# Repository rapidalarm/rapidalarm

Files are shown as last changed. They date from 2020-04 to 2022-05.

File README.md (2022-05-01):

# Illinois RapidAlarm: Emergency ventilator sensor and alarm system

*Developed at the Grainger College of Engineering at the University of Illinois at Urbana-Champaign with support from Carle Health and Creative Thermal Solutions, Inc.*

Illinois RapidAlarm

The Illinois RapidAlarm is a sensor and alarm module for use with emergency pressure-cycled ventilators such as the [Illinois RapidVent](https://rapidvent.grainger.illinois.edu/). More information and documentation is available at the [Illinois RapidAlarm project website](http://rapidalarm.github.io).

2020 Copyright University of Illinois Board of Trustees. Software is licensed under the MIT License; all other designs and documentation are licensed under the CC BY 4.0 license: https://creativecommons.org/licenses/by/4.0/

Please see the [legal disclaimer](https://rapidalarm.github.io/#!legal.md) on the project website.

### Repository Structure

- `code/` - firmware for monitor ATMega, simulations
  - `data/` - labeled alarm test data from artificial lung
  - `firmware/` - ATmega328 alarm firmware
  - `rapidalarm/` - Python plotting tools and test suite
- `cad/` - mechanical CAD files, enclosures, etc.
    - `enclosure_lasercut/` - enclosure design files for lasercutter
    - `enclosure_3dprint/` - enclosure design files for 3d printer
- `pcb/` - KiCAD design files
  - `pcb_proto/` - through hole board variant, based on ATmega328
  - `pcb_smd/` - surface mount board variant, based on ATmega32u4

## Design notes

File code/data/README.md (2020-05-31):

# rapidalarm test data

### File structure

- `raw/` - raw data recordings
- `ventmap_0282.csv` - Human trial data converted from ventMAP

### CSV Format

The first two lines of the CSV file contain information about sample rate and column names

e.g.

    #samplerate,50
    pressure,flow,true_pip,true_peep,true_rr
    10.57,3.44,20.57,10.879999999999999,14.084507042253522
    10.55,5.36,20.57,10.879999999999999,14.084507042253522
    10.51,9.18,20.57,10.879999999999999,14.084507042253522
    ...
    
`true_pip`, `true_peep`, `true_rr` refer to reported values from the professional ventilator.  Only available in the ventmap datasets.

### ventMAP Data

A lot of human-trial ventilator waveform data can be found in the [ventMAP project repo](https://github.com/hahnicity/ventMAP/tree/master/ventmap/tests/samples), albeit a bit disorganized.  This includes waveforms from a few modes of ventilation.

These recordings were made using the PB-840 ventilator at 50Hz.  You can use the `ventmap2csv.py` tool to convert these `.csv_test` files into the csv format used by the rapidalarm Python library.

    python ventmap2csv.py raw/ventmap/0282dbl_diff.csv_test ventmap_0282.csv

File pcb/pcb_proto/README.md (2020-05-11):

# pcb_proto

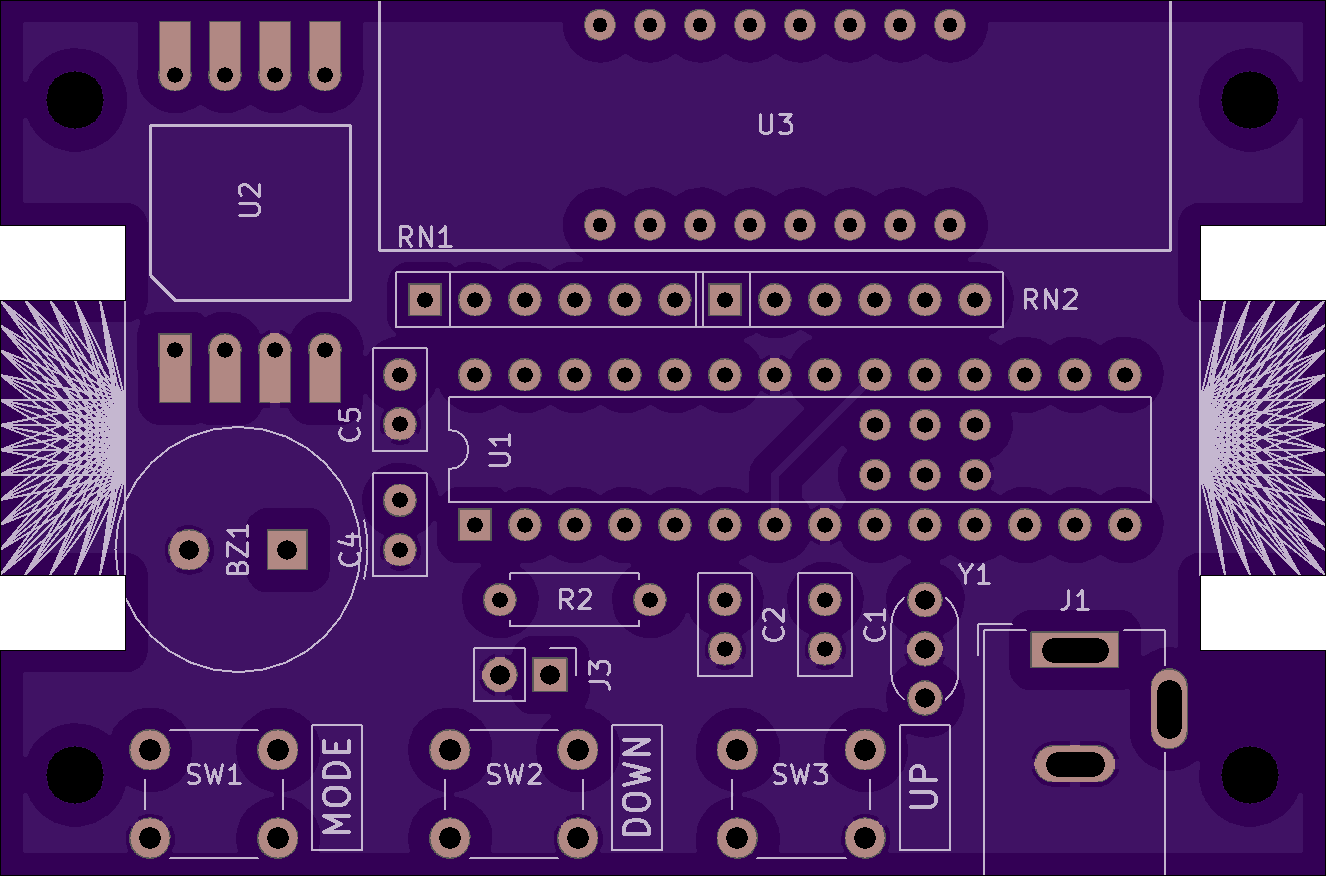
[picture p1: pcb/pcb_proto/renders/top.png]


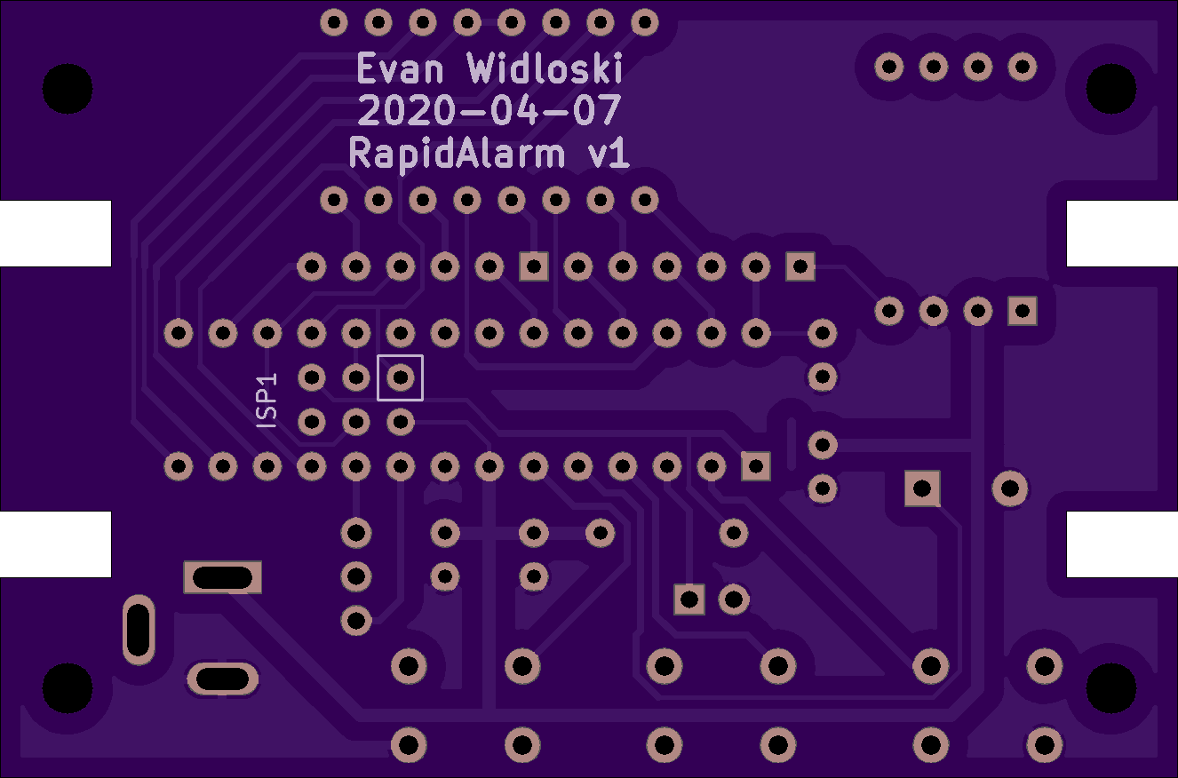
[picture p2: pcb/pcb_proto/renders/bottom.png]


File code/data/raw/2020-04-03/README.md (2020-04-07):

This data is in the same format as the data from 2020-04-01, but sampled at 100Hz.

- low_rate - PIP and rate knobs adjusted so that respiratory cycle is too long
- noncompliant - false lung manually squeezed so that breaths are shallow and too fast

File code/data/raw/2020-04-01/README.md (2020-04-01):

# Sample Data 2020-04-01

- `exit_port_leak` - opened then closed hole near exit port, bypassing rate valve
- `lung_disconnect` - disconnected then reconnected false lung
- `lung_partial_disconnect` - loosely disconnected then reconnected false lung, (lung stopped cycling and remained inflated)
- `source_disconnect` - complete disconnect then reconnect of pressured air

This is sample data from tests with the ventilator setup at CTS.  Data was sampled in a free running loop at approximately 133Hz.  Columns 1 and 2 correspond to pitot tube pressure and wall pressure, respectively.

To convert the measurements to cm H20, use the expression

    10.197 * (x / 1024 - 0.04) / 0.09

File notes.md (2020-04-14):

### Transducers

| Part       | Digikey Quantity | Mouser Quantity |
| ---------- | -------          | ------          |
| MPXV5100GC | 756              | 1029            |
| MPXV5100GP | 292              |                 |
| MPXV5100DP | 4500             | 2881            |
| MPXV5050GC |                  | 2820            |
| MPXV5050DP | 379              | 404             |
| MPXV7025   | 279              | 8264            |
| MPXV5010GC | 420              |                 |
| MPVZ5010GW | 425              |                 |
| MPXV4006DP | 276              |                 |
| MPXV4006GC | 245              | 200             |
| MPXV5004   | 1320             |                 |

- sdp800-125
- https://octopart.com/2smpp-02-omron-18985974?r=sp#Specs
- https://octopart.com/tbpdans015pgucv-honeywell-34872416?r=sp
- https://octopart.com/mpvz4006gw7u-nxp+semiconductors-70303583?r=sp
- differential sensors ~.01psi/1cmh20 - https://www.digikey.com/products/en/sensors-transducers/pressure-sensors-transducers/512?k=pressure+sensor&k=&pkeyword=pressure+sensor&sv=0&pv144=8614&pv144=6360&pv144=4027&pv144=2964&pv144=620&pv144=640&pv144=427967&pv144=650&pv144=662&pv144=666&pv144=683&pv144=427968&pv144=694&pv144=425047&pv144=719&pv144=725&pv144=728&pv144=729&pv144=427966&pv144=427965&pv144=786&pv144=6350&pv144=6876&pv144=427804&pv144=8073&pv144=8612&pv144=8613&pv144=8289&pv144=9508&pv276=174378&pv276=228720&pv276=206234&pv276=208636&pv276=208699&pv276=209065&pv276=209787&pv276=209799&pv276=209898&pv276=209941&pv276=209952&pv276=210520&pv276=211233&pv276=249171&pv276=249294&pv276=249306&pv276=249369&pv276=249379&sf=1&FV=-8%7C512&quantity=&ColumnSort=0&page=1&stock=1&pageSize=500
- [venturi tube calculator](https://www.pipeflowcalculations.com/venturi/calculator.xhtml)

### M. Stevens Questions

- considerations for pick-and-place
- local pick-and-place machines

- tvs diodes on buttons
- high esr bulk cap on supply
- wall wart has built-in mov
- panelizing design
- 062
- vscore 1 mil

#### Flow transducers
- https://octopart.com/d6f-ph0505ad3-omron-29408017?r=sp

### Things to Order
- https://www.digikey.com/product-detail/en/te-connectivity-alcoswitch-switches/2-1825910-7/450-1642-ND/1632528
- https://octopart.com/2smpp-02-omron-18985974?r=sp#Specs
- https://octopart.com/tbpdans015pgucv-honeywell-34872416?r=sp
- https://octopart.com/mpvz4006gw7u-nxp+semiconductors-70303583?r=sp

### Ordered
- https://www.digikey.com/short/zpq87p

- voltage reference 1.234V, 5x - https://www.digikey.com/product-detail/en/texas-instruments/LM385BLP-1-2/296-9558-5-ND/379850
- voltage reference 3V, 5x - https://www.digikey.com/product-detail/en/texas-instruments/LM4040D30ILPR/296-21583-1-ND/1494038
- resistor array, 10x - https://www.digikey.com/product-detail/en/bourns-inc/4608X-102-471LF/4608X-2-471LF-ND/1089144
- resistor array, 10x - https://www.digikey.com/product-detail/en/bourns-inc/4606X-102-681LF/4606X-2-681LF-ND/1089048
- 4 digit display, 2x - https://www.digikey.com/product-detail/en/lite-on-inc/LTC-4627JF/160-1548-5-ND/408221
- inductor, 10x - https://www.digikey.com/product-detail/en/bourns-inc/78F100J-TR-RC/78F100J-TR-RCCT-ND/6679613
- barrel supply, 2x - https://www.digikey.com/product-detail/en/phihong-usa/PSM03A-050-R/993-1236-ND/4031882
- barrel jack, 3x - https://www.digikey.com/product-detail/en/w%C3%BCrth-elektronik/694106301002/732-5930-ND/5047522
- micro usb, 3x - https://www.digikey.com/product-detail/en/w%C3%BCrth-elektronik/629105150521/732-5960-1-ND/5047555
- buttons, 20x - https://www.digikey.com/product-detail/en/c-k/PTS636-SK43-LFS/CKN12303-ND/10071716
- pressure transducer, 1x - https://www.digikey.com/product-detail/en/nxp-usa-inc/MPXV5050GC6T1/568-13603-2-ND/2186550
- pressure transducer, 1x - https://www.digikey.com/products/en?keywords=mpxv5100dp
- pressure transucer, 1x - https://www.digikey.com/product-detail/en/nxp-usa-inc/MPXV7002DP/MPXV7002DP-ND/1168436
  
### Design questions

- shield vs dedicated board - shield about same cost with added benefit of extensibility -> slightly larger, more complex
  - produce dedicated in quantity, design shield produce small amount
- smd vs thru hole
  - a
- reprogrammability - maybe, pogo pin port on back of board
  - dont care
- sourcing transducers
- serial printing/debugging - no, requires switch from atmega or serial-usb interface chip
- power connector - micro usb?  convenient for low quant, more difficult to solder than barrel

- alarm - SFM-27 https://www.youtube.com/watch?v=LLGMlErc0yQ
- esp8266 bulk US - https://www.ebay.com/itm/5X-ESP8266-ESP-12E-802-11n-WIFI-USB-Development-Board-Arduino-MicroPython-5-Pack/132532596048?hash=item1edb8eed50:g:Z3QAAOSwsnVdyOf-

- esp8266 bulk 
  - https://www.aliexpress.com/item/32665100123.html?spm=a2g0o.productlist.0.0.3ffc15495JaD23&algo_pvid=1e29147f-2a71-40df-94b8-4b58d9622e4f&algo_expid=1e29147f-2a71-40df-94b8-4b58d9622e4f-0&btsid=0ab6d69f15850880382543898e3676&ws_ab_test=searchweb0_0,searchweb201602_,searchweb201603_
  
- esp02 bulk
  - https://www.mouser.com/ProductDetail/Espressif-Systems/ESP-WROOM-02?qs=sGAEpiMZZMsRr7brxAGoXSSUPDSAjAiVc55QyFq0cPAl59eVNM2ypQ%3D%3D
  - https://www.digikey.com/product-detail/en/espressif-systems/ESP-WROOM-02/1904-1009-1-ND/8544304
  
- esp32 bulk
  - https://www.mouser.com/ProductDetail/Espressif-Systems/ESP32-WROOM-32-16MB?qs=sGAEpiMZZMsRr7brxAGoXSSUPDSAjAiVWYDCG5gOE4CudLdUnuGgeQ%3D%3D
  - https://www.mouser.com/ProductDetail/Espressif-Systems/ESP32-SOLO-1?qs=sGAEpiMZZMsRr7brxAGoXSSUPDSAjAiVLQnuuMBfLkMt7n12ghVrZw%3D%3D
  - https://www.digikey.com/product-detail/en/espressif-systems/ESP32-WROVER/1904-1007-1-ND/8544302

- kivy signed build - https://groups.google.com/forum/#!topic/kivy-users/pBtbg8aSlNo
- kivy listview update - https://groups.google.com/forum/#!topic/kivy-users/D7kaXll-rj8

huge dirs:

- ~/.local/share/python-for-android
- ~/.buildozer

### when to raise alarm

- respiratory rate too high or too low

### Definitions

- [ventilator control modes](https://www.youtube.com/watch?v=gk_Qf-JAL84)
- [respiratory cycle example](https://www.youtube.com/watch?v=K0maLgTzIto)
- [pressure control ventilation](https://www.youtube.com/watch?v=h-I6XE6EfMY)

- WOB - work of breathing - 
- compliance - ΔV/ΔP - analogous to stiffness constant of spring (inverted)
- restrictive lung disease - condition in which compliance of lung is reduced.  Greater pressure needed to deliver same volume of air
- FIO2 - fractional inspiration of oxygen - percent of air volume oxygen
- CMV - continuous mandatory control
- IMV - intermittent mandatory control
- TCT - total cycle time (60 / rate)
- Ti - inspiration time
- Te - expiration time
- PC - pressure control
- AC - assist control
- PEEP - positive-end expiratory pressure

- ventilator modes
  - AC - assist control - ventilator control mode where specific volume is delivered to patient in each cycle
    - patient triggers ventilator
    - set tidal volume, instantaneous pressure dependent on lung compliance
    - e.g. 500-600cc of air delivered (8mL/kg bodyweight)
  - PC - pressure control - 
    - patient or ventilator trigger inspiration
    - set tidal pressure, instantaneous volume dependent on lung compliance
    - if compliance of lungs changes, inspired volume can change
  - CPAP - non-invasive ventilation, facemask instead of tracheal tube, sleep apnea
    - devices often have a PEEP setting
    - PEEP - positive-end expiratory pressure - positive pressure setting after expiration
      - prevents sleep apnea, tongue back
      - keeps alveoli open
      - set pressure (cm water pressure, e.g. 5-20 cm)
  - PS - pressure support
    - patient initiates all breaths (e.g. 5-15 cm pressure)
    
- 

### Example Orders for Ventilator
- AC 16 - assist control, backup rate 16 breaths per minute
  - rate: 16
  - tidal volume: 550mL
  - FIO2: 50%
  - PEEP: 5
  - optional: inspiratory flow
  
- PC
  - pressure control level (defined absolutely or amount above PEEP)
  - rate
  - Ti (amount of time pressure held high?)
  - PEEP
  - FiO2
  - Sensitivity

### Problems in AC Mode Ventilation

- [detecting respiratory cycle problems](https://www.youtube.com/watch?v=6Bdv7QhNNy4)

- assist control
  - high peak pressure (poor airway flow) (also called Pplat, MAP mean error press., Paw peak airway)
    - bronchiospasms
    - secretions
    - mucus plug
    - tracheal tube occlusion
  - high plateau pressure (low lung compliance)
    - pneumothorax
    - pulmonary edema
    - ARDS
    - pneumonia

### Old Purchases
- displays
    - 2x - https://www.digikey.com/product-detail/en/lite-on-inc/LTC-4627JF/160-1548-5-ND/408221
- transducers
    - 2x - https://www.digikey.com/product-detail/en/nxp-usa-inc/MPXV5010GC7U/MPXV5010GC7U-ND/412949
    - https://www.digikey.com/product-detail/en/nxp-usa-inc/MPXV7007DP/MPXV7007DP-ND/1168438
    - https://www.digikey.com/product-detail/en/nxp-usa-inc/MPXV5010DP/MPXV5010DP-ND/531280
- buzzers
    - https://www.digikey.com/product-detail/en/pui-audio-inc/AI-3035-TWT-3V-R/668-1204-ND/1745457
    - 2x - https://www.digikey.com/product-detail/en/murata-electronics/PKM13EPYH4002-B0/490-4697-ND/1219328
- microcontrollers
    - https://www.digikey.com/product-detail/en/espressif-systems/ESP32-WROOM-32/1904-1010-1-ND/8544305
    - 2x - https://www.digikey.com/product-detail/en/microchip-technology/ATMEGA328P-PU/ATMEGA328P-PU-ND/1914589
    - https://www.digikey.com/product-detail/en/microchip-technology/ATMEGA328P-AUR/ATMEGA328P-AURCT-ND/3789455
- tactile switch
    - 6x - https://www.digikey.com/product-detail/en/omron-electronics-inc-emc-div/B3FS-1000P/SW423CT-ND/277814
    
- old stuff, dont order
    - https://www.digikey.com/product-detail/en/varitronix/VI-201-DP-RC-S/153-1003-ND/2375
    - https://www.digikey.com/product-detail/en/matrix-orbital/MOP-AL162A-BBTW-25J-3IN/635-1206-ND/9602839
    - https://www.digikey.com/product-detail/en/adafruit-industries-llc/1001/1528-1513-ND/5774239
    - https://www.digikey.com/product-detail/en/newhaven-display-intl/NHD-C0216CZ-FSW-FBW-3V3/NHD-C0216CZ-FSW-FBW-3V3-ND/2059234

### Power Supply
- https://www.digikey.com/products/en/power-supplies-external-internal-off-board/ac-dc-desktop-wall-adapters/130?k=power+supply&k=&pkeyword=power+supply&sv=0&sf=0&FV=-8%7C130&quantity=&ColumnSort=1000011&page=1&stock=1&pageSize=25

### Display Modules
- 3.3V, Serial, $8 - https://www.digikey.com/product-detail/en/newhaven-display-intl/NHD-C0216CZ-FSW-FBW-3V3/NHD-C0216CZ-FSW-FBW-3V3-ND/2059234
-

### Differential pressure sensors

##### Single-Ended
| Part        | Price | Quantity | Voltage | Range | Notes      |
| MPXV4006GC6 |       |          | 5V      | 60cm  | Integrated |
| MP3V5004GP  |       | 5000     | 3V      | 40cm  | Integrated |
| MPX5010GP   |       |          |         |       |            |

##### Differential

| Part        | Price | Quantity | Voltage | Range | Notes         |
| MP3V5004DP  |       |          | 3V      | 40cm  | Integrated    |
| MPX10DP     |       |          | 3V      | 100cm | Uncompensated |
| MP3V5010DP  |       |          | 3V      | 100cm | Integrated    |
| MPXV5010DP  |       |          | 5V      | 100cm | Integrated    |
| MP3V5004GC6 |       |          |         | 40    |               |
| MP3V5010GC6 |       |          | 3V      | 100cm | Integrated    |

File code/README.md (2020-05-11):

### Directory Structure

- `firmware/` - monitor firmware
- `rapidalarm/` - alarm algorithm test suite
- `data/` - test data

### Installation

Clone this repo.  From the `code/` directory:

Linux/OSX

    pip install .
    
Windows

1. [Install Visual C++ build tools](https://visualstudio.microsoft.com/visual-cpp-build-tools/)
2. Restart
3. Run the above

### Usage

Run algorithm on recorded ventilator waveform and plot PIP/PEEP estimates

    rapidalarm plot data/ventmap_0282.csv
    
Alternatively you can import the library and do your own investigation

    >>> from rapidalarm.rapidalarm import run_pandas
    >>> df = run_pandas('data/ventmap_0282.csv')
    
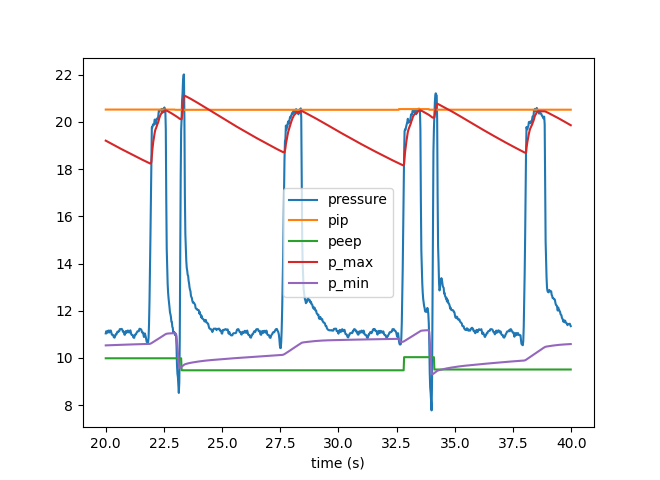
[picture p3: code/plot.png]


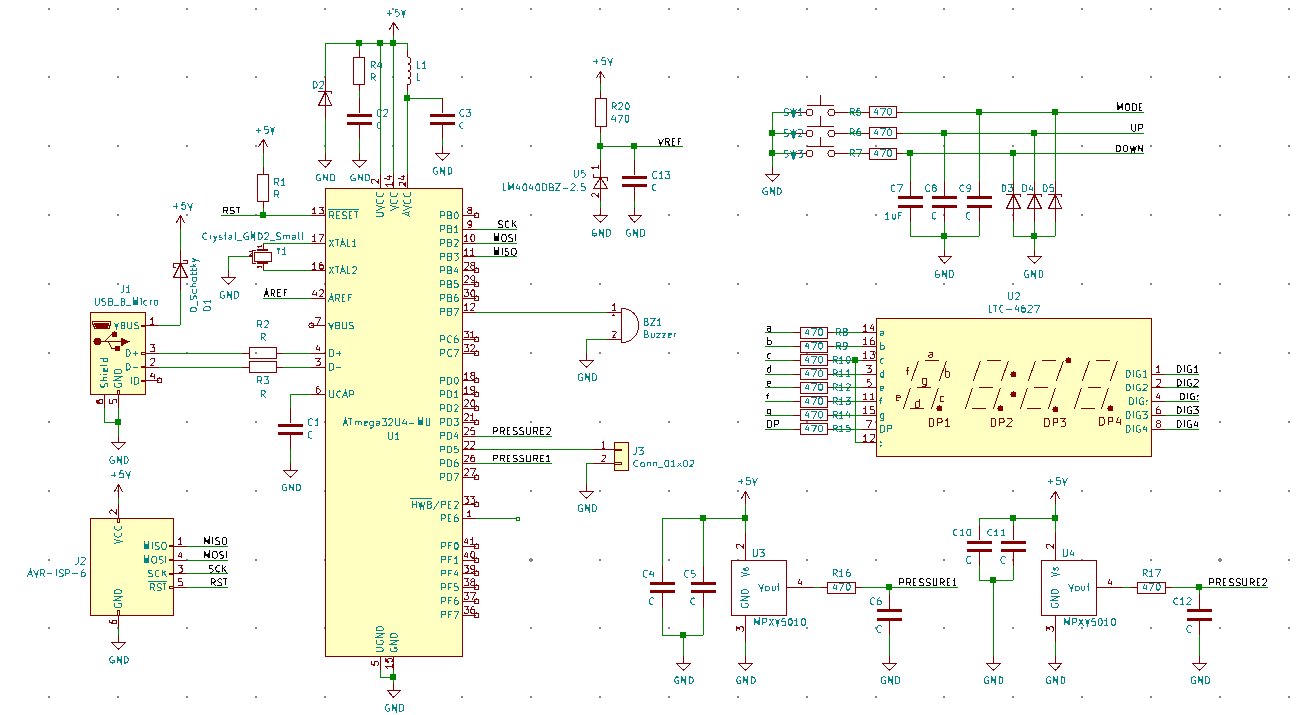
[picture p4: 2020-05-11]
pcb/pcb_smd/schematic.png

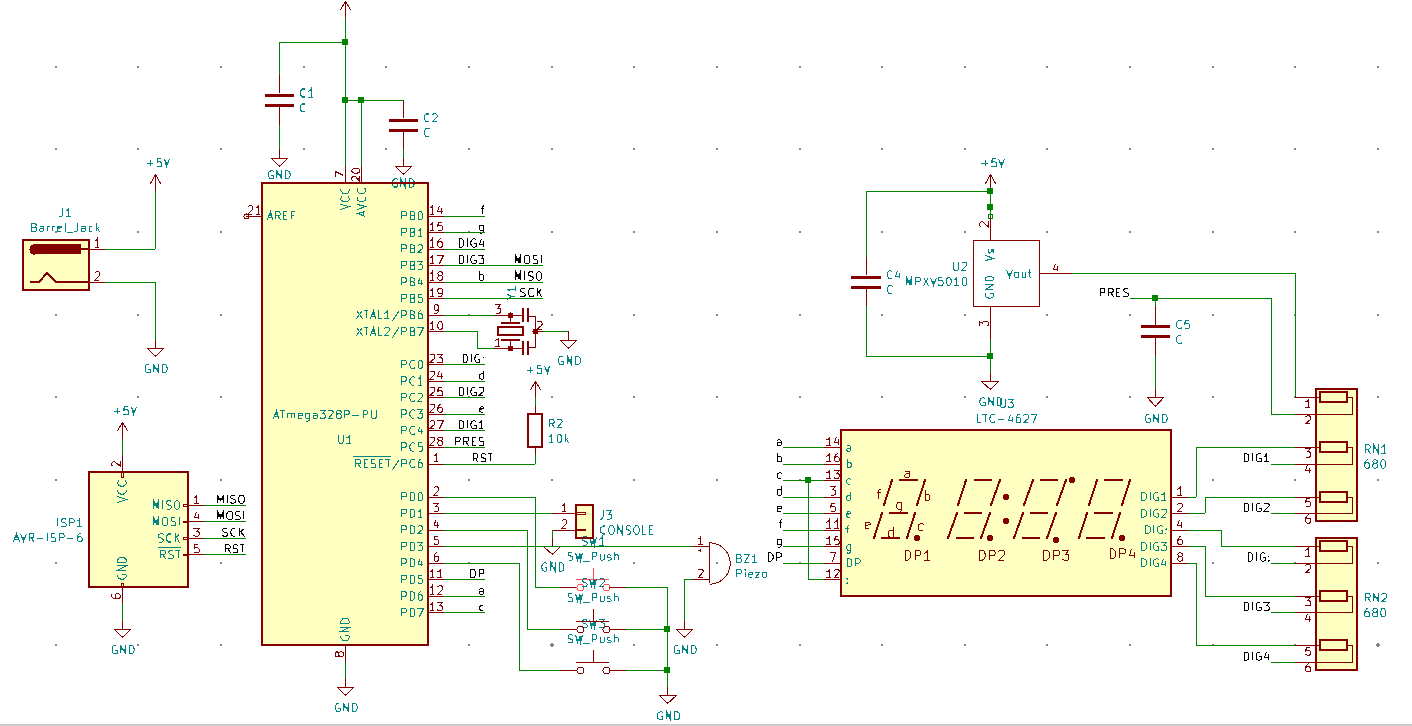
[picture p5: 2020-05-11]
pcb/pcb_proto/schematic.png

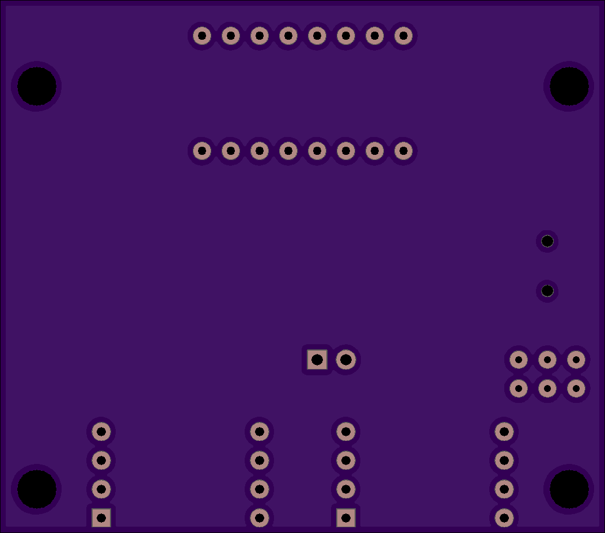
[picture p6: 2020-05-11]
pcb/pcb_smd/renders/bottom.png

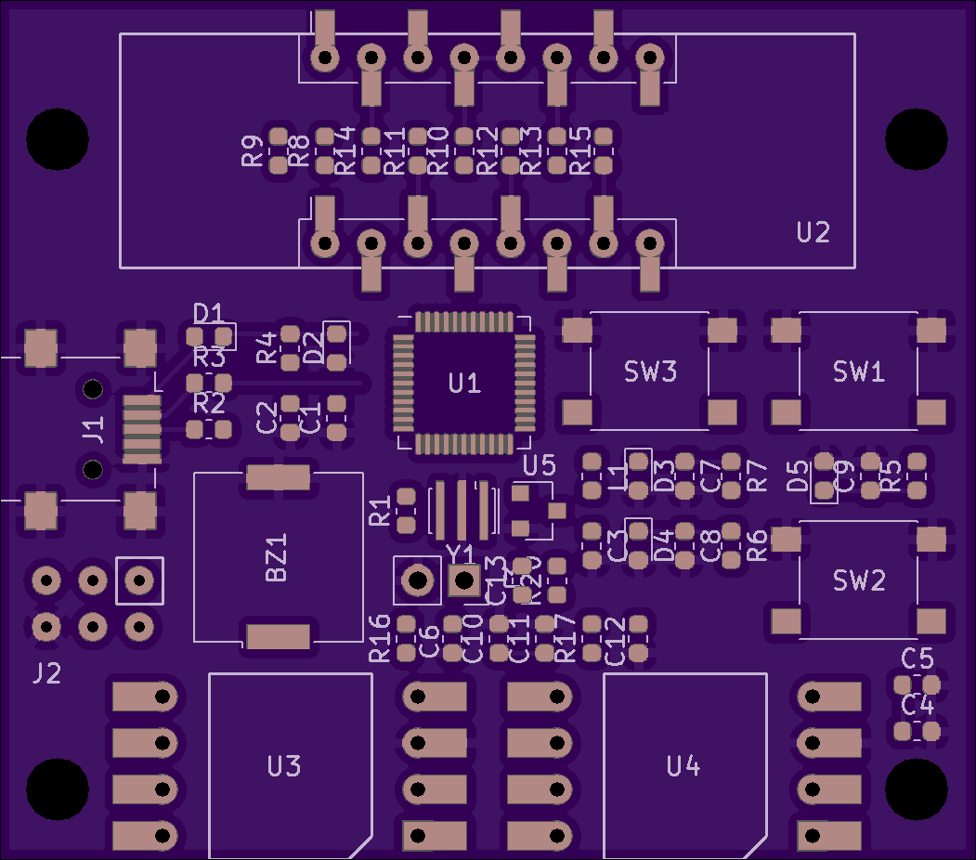
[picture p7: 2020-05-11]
pcb/pcb_smd/renders/top.png

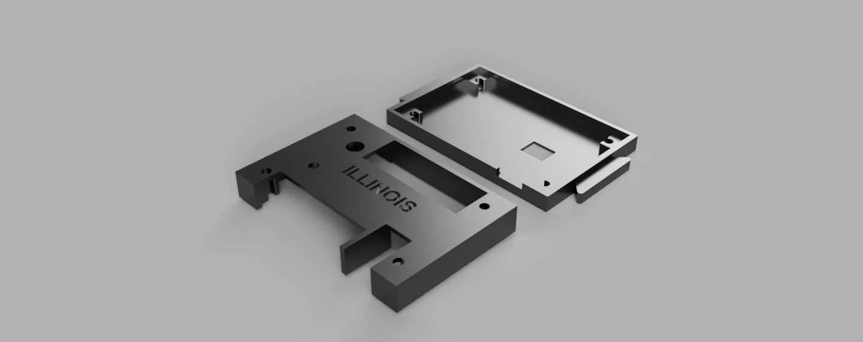
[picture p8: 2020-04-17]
cad/enclosure_3Dprint/alarm_housing.png

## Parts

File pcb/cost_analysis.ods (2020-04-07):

Name | Cost | Quantity | Area | Link
 |  |  |  |  | Oshpark cost per inch | 1
Essential Parts
7 segment | 1.74 | 1
MPX5010 | 9.25 | 1
Buttons | 0.15 | 3
ATmega DIP
atmega | 1.73 | 1
Thru-hole resonator | 0.11 | 1 |  | https://www.digikey.com/product-detail/en/murata-electronics/CSTLS8M00G53-B0/490-1212-ND/584420
Board | 3.57 |  | 3.57
Micro USB | 0.5 | 1
Total | 17.05
Uno/Nano Shield
Board | 4.62 |  | 4.62
Total | 15.76
Uno/Nano Shield w/ DIP
Board | 4.62 |  | 4.62
atmega | 1.73 | 1
Thru-hole resonator | 0.11 | 1
Micro USB | 0.5 | 1
Total | 18.1
Minimal Uno Shield
Board | 0.6 |  | 0.6
MPX5010 | 9.25 | 1
Buzzer | 0.25
Reference | 0.2
Total | 10.3

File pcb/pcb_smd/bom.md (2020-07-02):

- TVS diode - 10 - [link](https://www.digikey.com/product-detail/en/DF2S8.2ASL%2CL3F/DF2S8.2ASLL3FCT-ND/5415969/?itemSeq=331094759)
- Schottky diode - 10 - [link](https://www.digikey.com/product-detail/en/avx-corporation/SD0603S040S0R2/478-7798-1-ND/3749483)
- 470R - 100 - [link](https://www.digikey.com/product-detail/en/yageo/RC0603JR-07470RL/311-470GRCT-ND/729738)
- 10k - 100 - [link](https://www.digikey.com/product-detail/en/yageo/RC0603JR-0710KL/311-10KGRCT-ND/729647)
- 22R - 100 - [link](https://www.digikey.com/product-detail/en/te-connectivity-passive-product/CRGCQ0603J22R/A130081CT-ND/8577913)
- 1uF - 100 - [link](https://www.digikey.com/product-detail/en/samsung-electro-mechanics/CL10A105KP8NNNC/1276-1182-1-ND/3889268)
- 0.01uF - 100 - [link](https://www.digikey.com/product-detail/en/kemet/C0603C103M5RACTU/399-7842-1-ND/3471565)
- 47nH - 10 - [link](https://www.digikey.com/product-detail/en/johanson-technology-inc/L-14C47NJV4T/712-1442-1-ND/1914892)
- atmega32u4 - 2 - [link](https://www.digikey.com/product-detail/en/microchip-technology/ATMEGA32U4RC-AU/ATMEGA32U4RC-AU-ND/2507982)
- microusb - 2 - [link](https://www.digikey.com/product-detail/en/amphenol-icc-fci/10118192-0002LF/609-5379-1-ND/8555650)
- buzzer - 2 - [link](https://www.digikey.com/product-detail/en/murata-electronics/PKM13EPYH4002-B0/490-4697-ND/1219328)
- display - 2 - [link](https://www.digikey.com/product-detail/en/lite-on-inc/LTC-4627JF/160-1548-5-ND/408221)
- switch - 10 - [link](https://www.digikey.com/product-detail/en/te-connectivity-alcoswitch-switches/FSM14JSMAS/450-2161-ND/5343810)
- oscillator - 5 [link](https://www.digikey.com/product-detail/en/murata-electronics/CSTNE8M00G550000R0/490-17958-1-ND/8747766)

- pressure - 2 - [link](https://www.mouser.com/ProductDetail/NXP-Semiconductors/MPXV5010GP?qs=N2XN0KY4UWUfWoGX6cpzOg%3D%3D)
- pressure - 2 - [link](https://www.mouser.com/ProductDetail/NXP-Semiconductors/MPXV5010GC7U?qs=N2XN0KY4UWXJaisQ4tacmg%3D%3D)

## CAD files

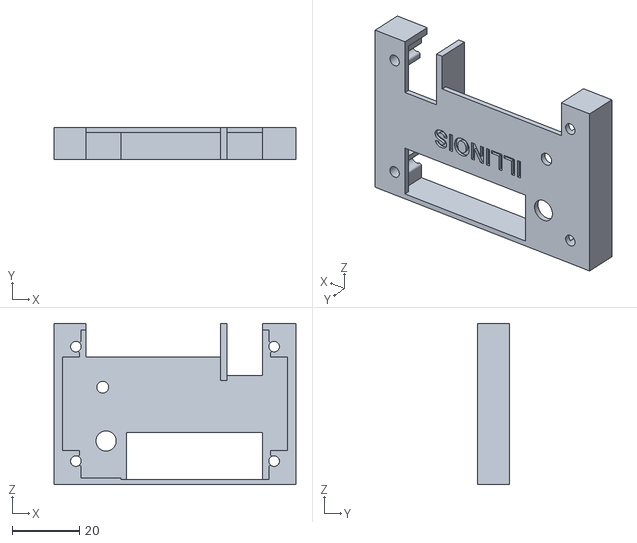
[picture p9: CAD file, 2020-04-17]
cad/enclosure_3Dprint/top.stl
72.0 x 9.50 x 48.0

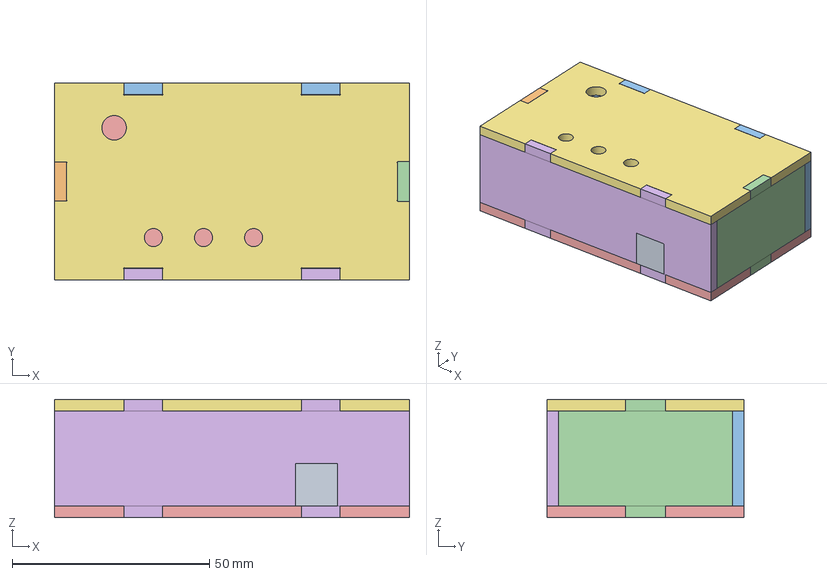
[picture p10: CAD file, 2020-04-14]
cad/enclosure_lasercut/enclosure.FCStd
90.0 x 50.0 x 30.0 mm
behind_panel_tab
right_panel_tab
face_panel_tab
left_panel_tab
bottom_panel_tab

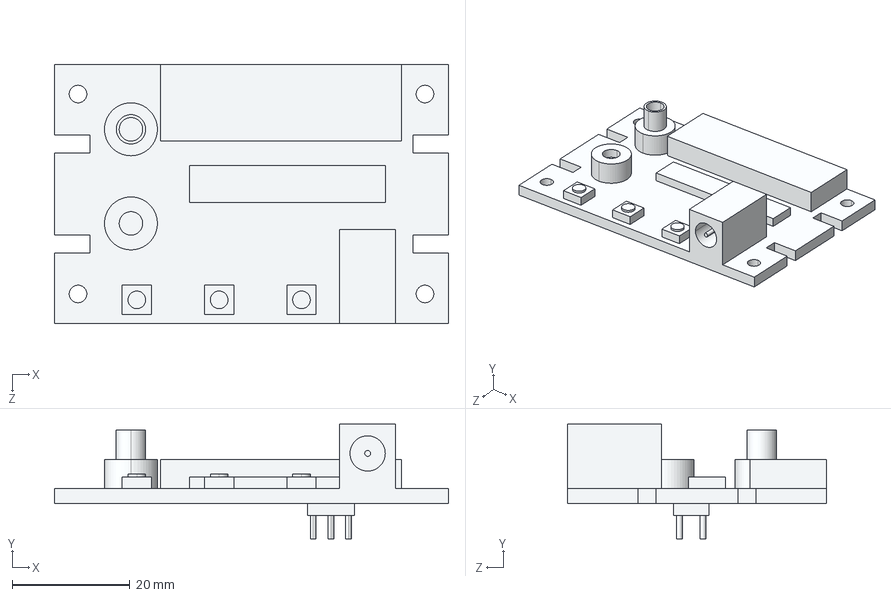
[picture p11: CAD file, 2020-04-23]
cad/enclosure_milled/MCH-00649.STEP
67.0 x 19.5 x 44.0 mm

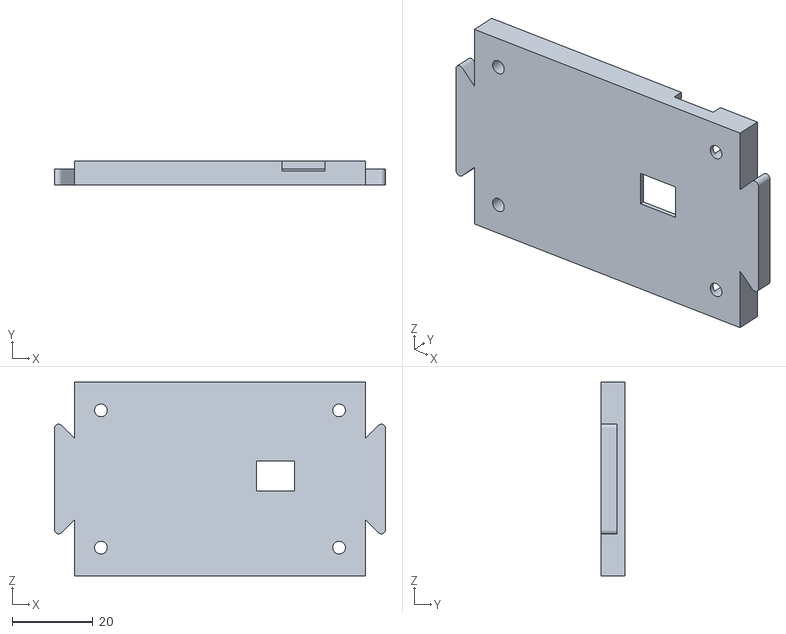
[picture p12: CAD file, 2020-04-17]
cad/enclosure_3Dprint/bottom.stl
82.0 x 6.00 x 48.0

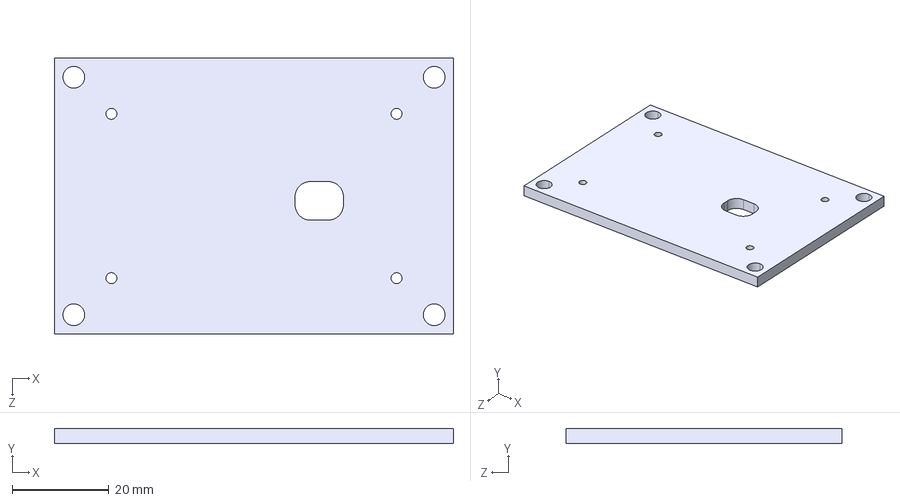
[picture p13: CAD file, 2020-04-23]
cad/enclosure_milled/MCH-00647.STEP
82.5 x 3.17 x 57.2 mm

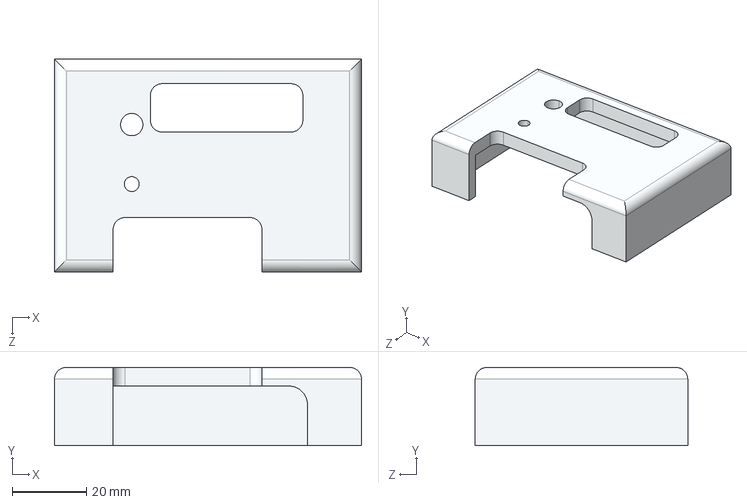
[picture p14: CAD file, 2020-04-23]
cad/enclosure_milled/MCH-00648.STEP
82.5 x 21.0 x 57.2 mm

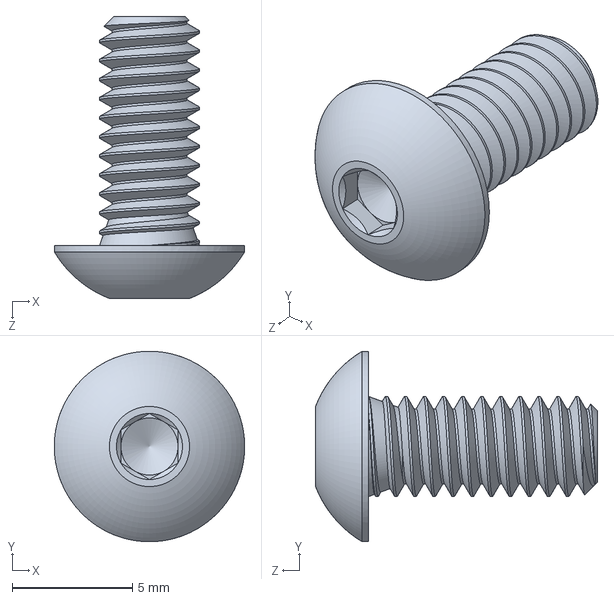
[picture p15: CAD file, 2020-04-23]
cad/enclosure_milled/92949A192_18-8 SS BUTTON HEAD HEX DRIVE SCREW.SLDPRT
7.92 x 7.92 x 11.7 mm

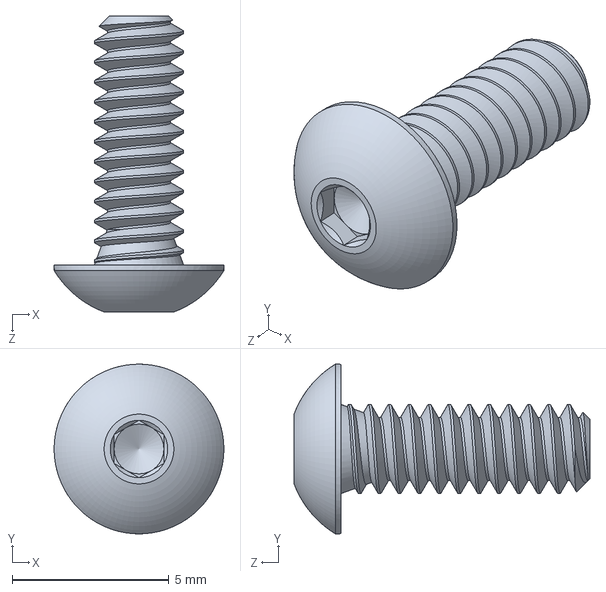
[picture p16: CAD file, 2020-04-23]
cad/enclosure_milled/92949A107_18-8 SS BUTTON HEAD HEX DRIVE SCREW.SLDPRT
5.41 x 5.41 x 9.44 mm

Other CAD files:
cad/enclosure_milled/MCH-00647.DXF
cad/enclosure_milled/MCH-00647.SLDDRW
cad/enclosure_milled/MCH-00647.SLDPRT
cad/enclosure_milled/MCH-00648.DXF
cad/enclosure_milled/MCH-00648.SLDDRW
cad/enclosure_milled/MCH-00648.SLDPRT
cad/enclosure_milled/MCH-00649.SLDPRT

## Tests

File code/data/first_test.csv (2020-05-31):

#samplerate | 133
pressure | flow | true_pip | true_peep | true_rr
12.396613281249998
12.396613281249998
12.396613281249998
12.396613281249998
12.507257812499997
12.396613281249998
12.396613281249998
12.28596875
12.396613281249998
12.507257812499997
12.728546874999997
12.839191406249999
13.171124999999998
13.50305859375
14.60950390625
16.15852734375
17.70755078125
18.482062499999998
18.37141796875
18.7033515625
18.924640625
19.36721875
19.47786328125
19.47786328125
19.588507812499998
19.92044140625
19.699152343749997
20.36301953125
20.252374999999997
20.141730468749998
20.36301953125
20.252374999999997
20.473664062499996
20.694953124999998
20.805597656249997
21.248175781249998
20.916242187499996
21.248175781249998
21.248175781249998
21.358820312499997
21.248175781249998
20.916242187499996
21.358820312499997
21.580109375
21.69075390625
21.69075390625
21.46946484375
21.69075390625
21.801398437499998
21.580109375
21.801398437499998
21.69075390625
21.801398437499998
21.91204296875
21.69075390625
21.46946484375
21.46946484375
21.69075390625
21.580109375
21.46946484375
21.580109375
21.91204296875
21.801398437499998
21.69075390625
21.91204296875
22.13333203125
22.022687499999996
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

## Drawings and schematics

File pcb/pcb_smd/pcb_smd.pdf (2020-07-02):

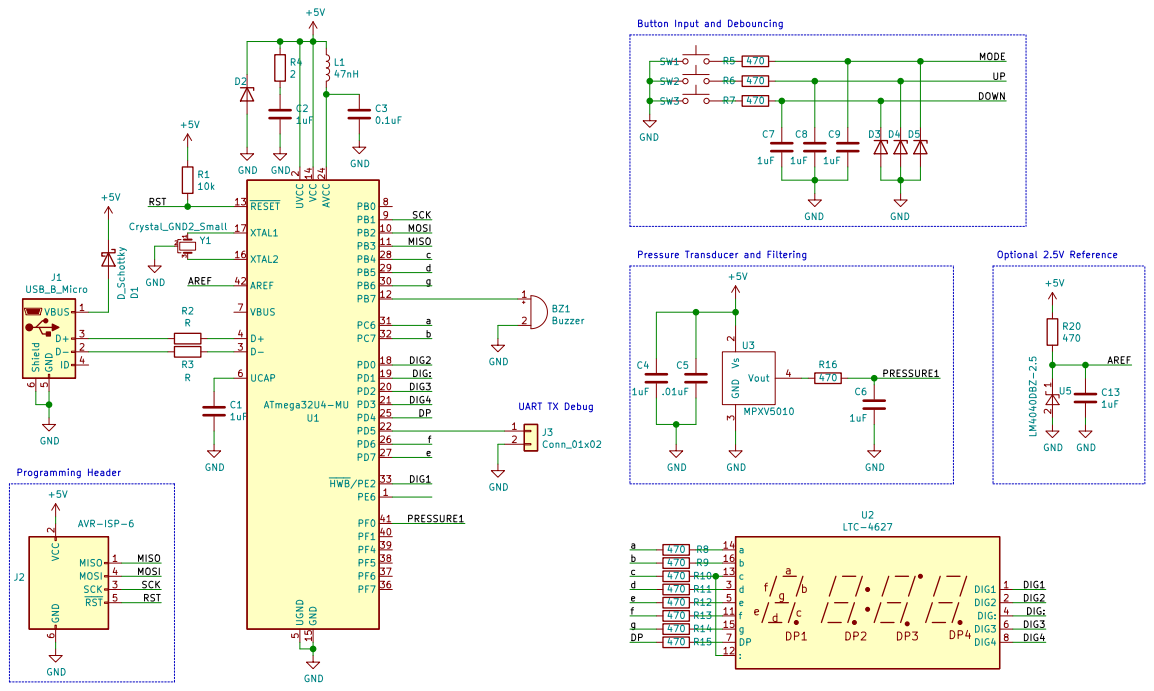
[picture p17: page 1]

Button Input and Debouncing

2 PD2 20 PD3 21 PD5 22 AVCC 24 PD4 25 PD6 26 PD7 27 PB4 28 PB5 29 D- 3 PB6 30 PC6 31 PC7 32 HWB/PE2 33 PF7 36 PF6 37 PF5 38 PF4 39 D+ 4 PF1 40 PF0 41 AREF 42 UGND

Pressure Transducer and Filtering

2 SCK 3 MOSI 4 RST 5 GND

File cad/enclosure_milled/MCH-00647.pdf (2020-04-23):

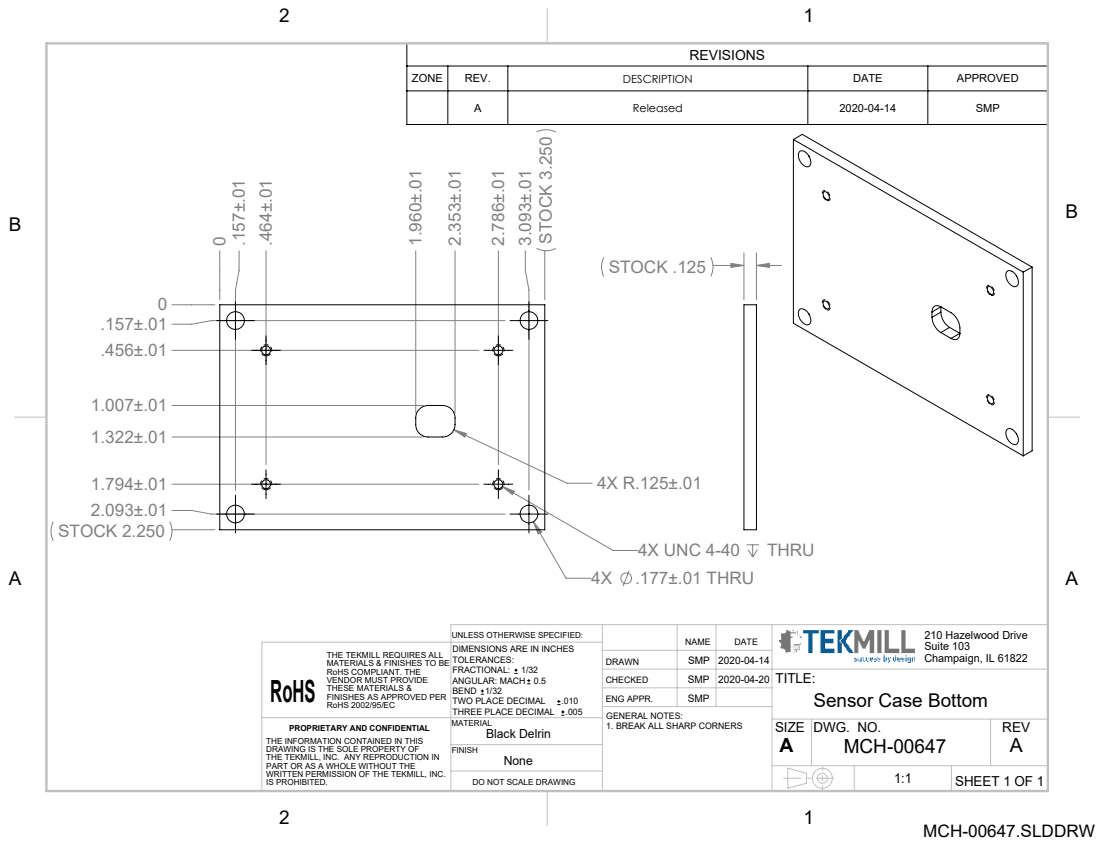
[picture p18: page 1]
4X .177±.01 THRU; 4X UNC 4-40 THRU; STOCK 3.250; STOCK 2.250; STOCK .125; Black Delrin; DO NOT SCALE DRAWING; SHEET 1 OF 1; DWG. NO.; REV; None FINISH; TWO PLACE DECIMAL; Sensor Case Bottom; 210 Hazelwood Drive Suite 103 Champaign, IL 61822

REVISIONS

ZONE | REV. | DESCRIPTION | DATE | APPROVED

A | Released | 2020-04-14 | SMP

UNLESS OTHERWISE SPECIFIED:
DIMENSIONS ARE IN INCHES
TOLERANCES:
FRACTIONAL: 1/32
ANGULAR: MACH 0.5
BEND 1/32
THREE PLACE DECIMAL .005
MATERIAL

THE TEKMILL REQUIRES ALL
MATERIALS & FINISHES TO BE
RoHS COMPLIANT. THE
RoHS

DRAWN
CHECKED
ENG APPR.
GENERAL NOTES:
1. BREAK ALL SHARP CORNERS

VENDOR MUST PROVIDE
THESE MATERIALS &
FINISHES AS APPROVED PER
RoHS 2002/95/EC

PROPRIETARY AND CONFIDENTIAL
THE INFORMATION CONTAINED IN THIS
DRAWING IS THE SOLE PROPERTY OF
THE TEKMILL, INC. ANY REPRODUCTION IN
PART OR AS A WHOLE WITHOUT THE
WRITTEN PERMISSION OF THE TEKMILL, INC.
IS PROHIBITED.

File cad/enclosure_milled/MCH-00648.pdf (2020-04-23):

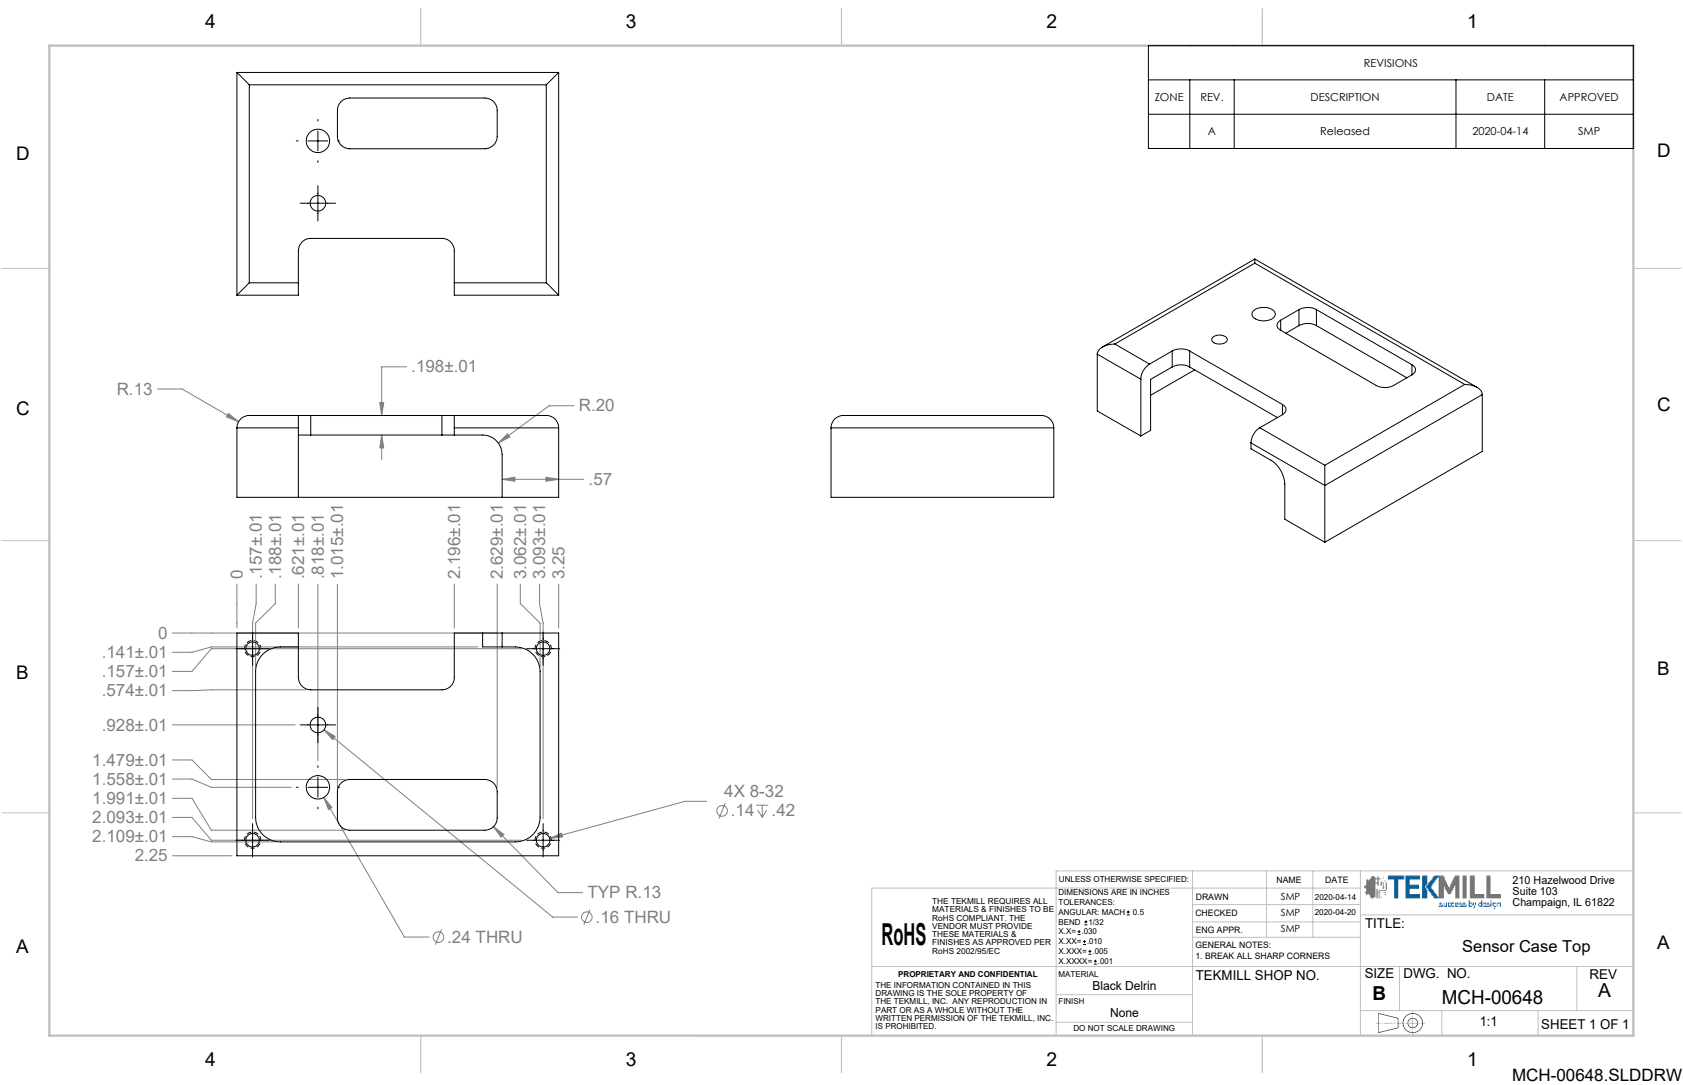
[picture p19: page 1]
.16 THRU; .24 THRU; TYP R.13; Black Delrin; DO NOT SCALE DRAWING; SHEET 1 OF 1; DWG. NO.; REV; Sensor Case Top

REVISIONS

ZONE | REV. | DESCRIPTION | DATE | APPROVED

A | Released | 2020-04-14 | SMP

UNLESS OTHERWISE SPECIFIED: | | NAME | DATE | 210 Hazelwood Drive Suite 103 Champaign, IL 61822

THE TEKMILL REQUIRES ALL MATERIALS & FINISHES TO BE RoHS RoHS COMPLIANT. THE VENDOR MUST PROVIDE THESE MATERIALS & FINISHES AS APPROVED PER RoHS 2002/95/EC | DIMENSIONS ARE IN INCHES TOLERANCES: ANGULAR: MACH 0.5 BEND 1/32 X.X= .030 X.XX= .010 X.XXX= .005 X.XXXX= .001 | DRAWN | SMP | 2020-04-14

CHECKED | SMP | 2020-04-20
ENG APPR. | SMP

GENERAL NOTES:
1. BREAK ALL SHARP CORNERS
TEKMILL SHOP NO.

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

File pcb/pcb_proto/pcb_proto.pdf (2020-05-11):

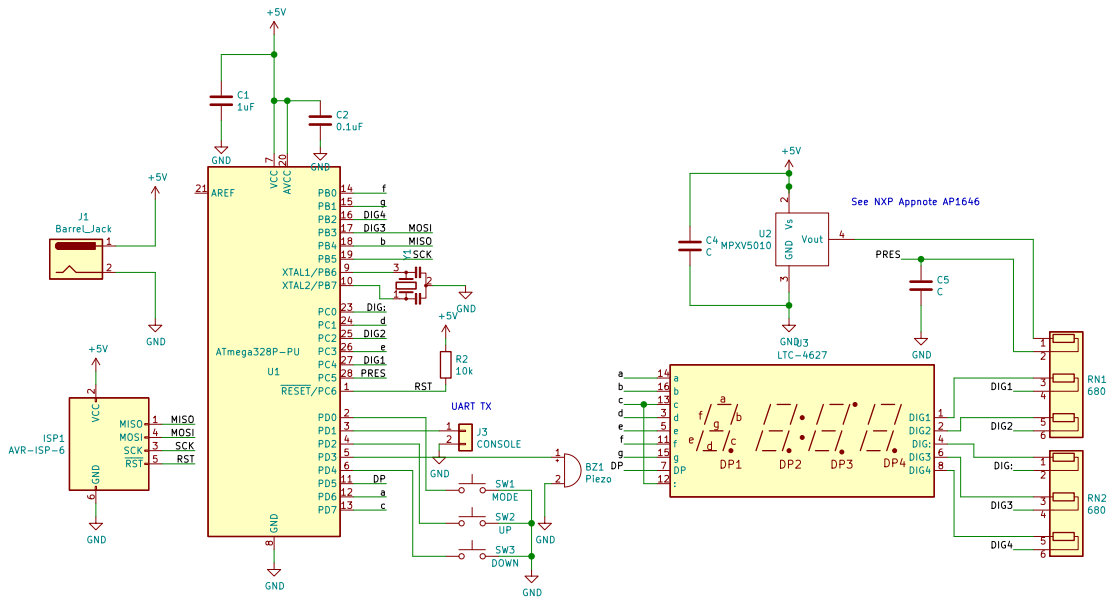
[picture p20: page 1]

2 SCK 3 MOSI 4 RST 5 GND

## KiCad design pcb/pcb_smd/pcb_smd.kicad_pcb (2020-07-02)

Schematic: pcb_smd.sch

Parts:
BZ1: Buzzer; Buzzer_Murata_PKMCS0909E4000-R1
C1, C2, C4, C6, C7, C8, C9, C13: 1uF; C_0603_1608Metric
C3: 0.1uF; C_0603_1608Metric
C5: .01uF; C_0603_1608Metric
D1: D_Schottky; D_0603_1608Metric
D2, D3, D4, D5: D_Zener; D_0603_1608Metric
J1: USB_B_Micro; USB_Mini-B_Lumberg_2486_01_Horizontal
J2: AVR-ISP-6; ISP_POGO
J3: Conn_01x02; PinSocket_1x02_P2.54mm_Vertical
J4: Conn_01x03; PinHeader_1x03_P2.54mm_Vertical
L1: 47nH; L_0603_1608Metric
R1: 10k; R_0603_1608Metric
R2, R3: 22; R_0603_1608Metric
R4: 2; R_0603_1608Metric
R5, R6, R7, R8, R9, R10, R11, R12, R13, R14, R15, R16, R20: 470; R_0603_1608Metric
SW1, SW2, SW3: SW_Push; SW_Push_1P1T_NO_6x6mm_H9.5mm
U1: ATmega32U4-MU; TQFP-44_10x10mm_P0.8mm
U2: LTC-4627; LTC-4627_SMD
U3: MPXV5010; DIPSOP-8_W550thou
U5: LM4040DBZ-2.5; SOT-23
Y1: Resonator; Resonator_SMD_muRata_CSTxExxV-3Pin_3.0x1.1mm_HandSoldering

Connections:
+5V: C4.1, C5.1, D1.1 (K), D2.1 (K), J2.2 (VCC), L1.1, R1.1, R4.1, R20.1, U1.2, U1.7, U1.14, U1.34, U3.2 (Vs)
/AREF: C13.1, R20.2, U1.42, U5.1
/DIG1: U1.33, U2.1 (DIG1)
/DIG2: U1.18, U2.2 (DIG2)
/DIG3: U1.20, U2.6 (DIG3)
/DIG4: U1.22, U2.8 (DIG4)
/DIG:: U1.19, U2.4 (DIG:)
/DOWN: C7.1, D3.1 (K), R7.1
/DP: R15.1, U1.25
/MISO: J2.1 (MISO), U1.11
/MODE: C9.1, D5.1 (K), R5.1
/MOSI: J2.4 (MOSI), U1.10
/PRESSURE1: C6.1, R16.2, U1.41
/RST: J2.5 (~RST), R1.2, U1.13
/SCK: J2.3 (SCK), U1.9
/UP: C8.1, D4.1 (K), R6.1
/a: R8.1, U1.31
/b: R9.1, U1.32
/c: R10.1, U1.28
/d: R11.1, U1.29
/e: R12.1, U1.27
/f: R13.1, U1.26
/g: R14.1, U1.30
GND: BZ1.2 (+), C1.1, C2.2, C3.2, C4.2, C5.2, C6.2, C7.2, C8.2, C9.2, C13.2, D2.2 (A), D3.2 (A), D4.2 (A), D5.2 (A), J1.5 (GND), J1.6 (Shield), J2.6 (GND), J3.2, J4.3, SW1.2, SW2.2, SW3.2, U1.5, U1.15, U1.23, U1.35, U1.43, U3.3 (GND), U5.2, Y1.2
unnamed: BZ1.1 (-), U1.12
unnamed: C1.2, U1.6
unnamed: C2.1, R4.2
unnamed: C3.1, L1.2, U1.24, U1.44
unnamed: D1.2 (A), J1.1 (VBUS)
unnamed: J1.2 (D-), R3.1
unnamed: J1.3 (D+), R2.1
unnamed: J3.1, U1.21
unnamed: J4.1, U1.37
unnamed: J4.2, U1.36
unnamed: R2.2, U1.4
unnamed: R3.2, U1.3
unnamed: R5.2, SW1.1
unnamed: R6.2, SW2.1
unnamed: R7.2, SW3.1
unnamed: R8.2, U2.14 (a)
unnamed: R9.2, U2.16 (b)
unnamed: R10.2, U2.12 (:), U2.13 (c)
unnamed: R11.2, U2.3 (d)
unnamed: R12.2, U2.5 (e)
unnamed: R13.2, U2.11 (f)
unnamed: R14.2, U2.15 (g)
unnamed: R15.2, U2.7 (DP)
unnamed: R16.1, U3.4 (Vout)
unnamed: U1.16, Y1.3
unnamed: U1.17, Y1.1

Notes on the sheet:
Programming Header
Extra
UART TX Debug
Button Input and Debouncing
Pressure Transducer and Filtering
Optional 2.5V Reference

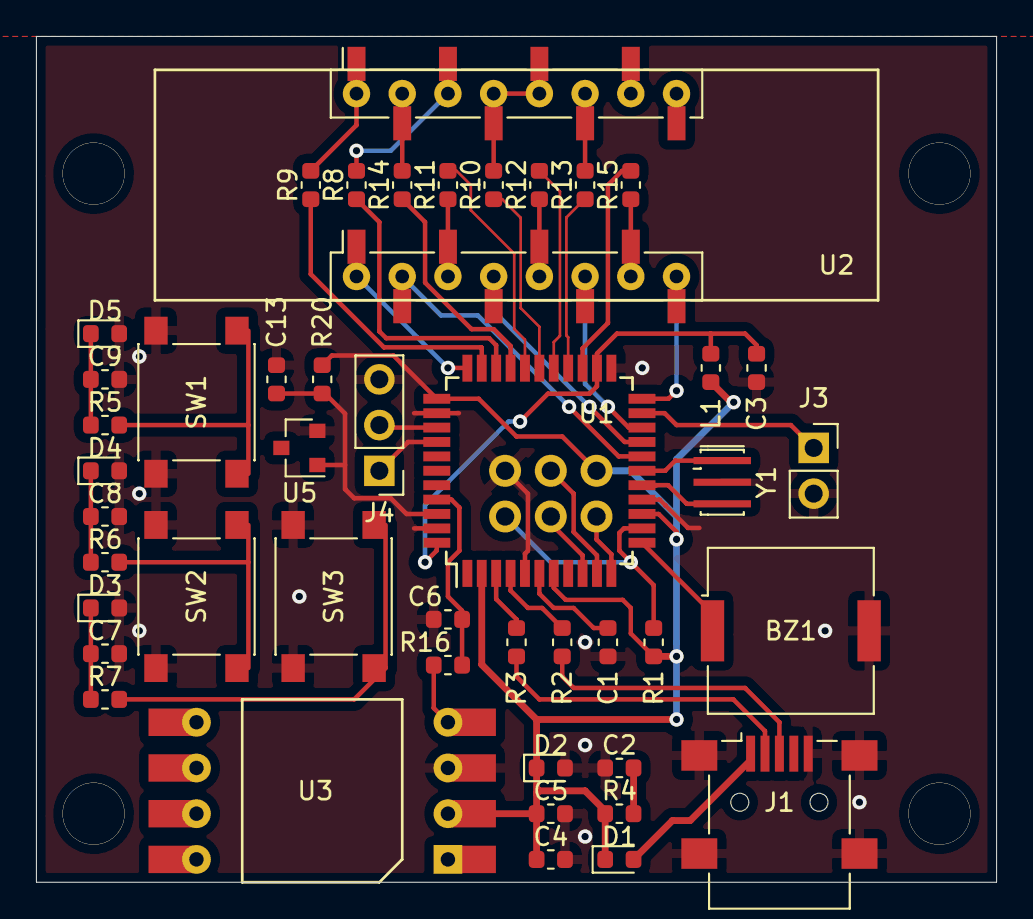
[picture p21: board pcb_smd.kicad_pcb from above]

Board: 2 copper layers, 53.3 x 47.0 mm, 46 parts (1 on the bottom side), 50 nets.

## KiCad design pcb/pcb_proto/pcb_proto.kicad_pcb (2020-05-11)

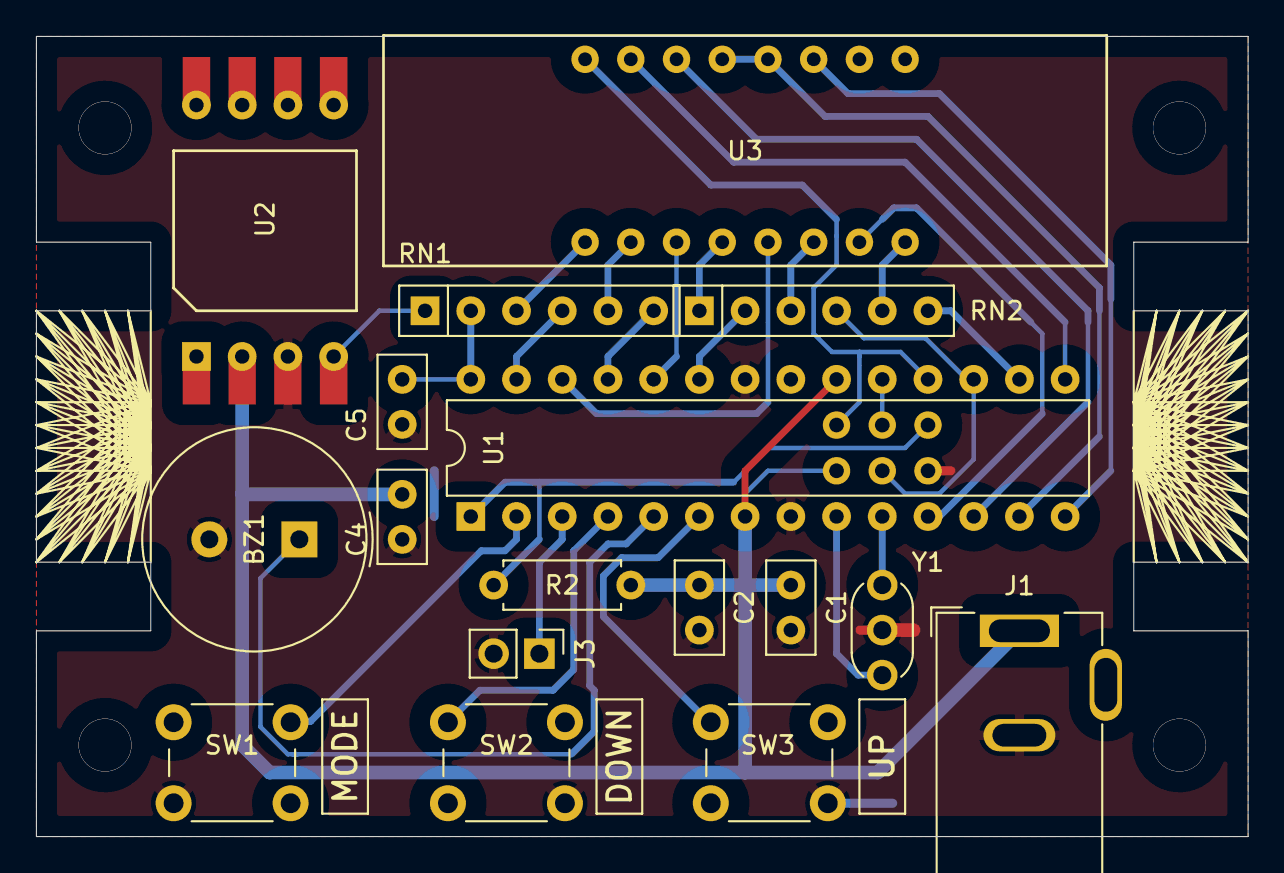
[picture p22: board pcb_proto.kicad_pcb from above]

Board: 2 copper layers, 67.3 x 44.5 mm, 18 parts (1 on the bottom side), 31 nets.

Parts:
BZ1: Piezo; Buzzer_TDK_PS1240P02BT_D12.2mm_H6.5mm
C1, C2, C4, C5: C; C_Disc_D5.0mm_W2.5mm_P2.50mm
ISP1: AVR-ISP-6; ISP_POGO
J1: Barrel_Jack; BarrelJack_Wuerth_6941xx301002
J3: CONSOLE; PinHeader_1x02_P2.54mm_Vertical
R2: 10k; R_Axial_DIN0207_L6.3mm_D2.5mm_P7.62mm_Horizontal
RN1, RN2: 680; R_Array_SIP6
SW1, SW2, SW3: SW_Push; SW_PUSH_6mm
U1: ATmega328P-PU; DIP-28_W7.62mm
U2: MPXV5010; DIPSOP-8_W550thou
U3: LTC-4627
Y1: Resonator_Small; Resonator_muRata_CSTLSxxxX-3Pin_W5.5mm_H3.0mm

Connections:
+5V: C1.1, C2.1, C4.1, ISP1.2, J1.1, R2.1, U1.7, U1.20, U2.2
/DIG1: RN1.4, U1.27
/DIG2: RN1.6, U1.25
/DIG3: ISP1.4, RN2.4, U1.17
/DIG4: RN2.6, U1.16
/DIG:: RN2.2, U1.23
/DP: U1.11, U3.7
/MISO: ISP1.1, U1.18, U3.16
/PRES: C5.1, RN1.2, U1.28
/RST: ISP1.5, R2.2, U1.1
/SCK: ISP1.3, U1.19
/a: U1.12, U3.14
/c: U1.13, U3.12, U3.13
/d: U1.24, U3.3
/e: U1.26, U3.5
/f: U1.14, U3.11
/g: U1.15, U3.15
GND: BZ1.2, C1.2, C2.2, C4.2, C5.2, ISP1.6, J1.2, J3.2, SW1.4, SW2.2, SW3.2, U1.8, U1.22, U2.3, Y1.2
unnamed: BZ1.1, U1.5
unnamed: J3.1, U1.3
unnamed: RN1.1, U2.4
unnamed: RN1.3, U3.1
unnamed: RN1.5, U3.2
unnamed: RN2.1, U3.4
unnamed: RN2.3, U3.6
unnamed: RN2.5, U3.8
unnamed: SW1.3, U1.2
unnamed: SW2.1, U1.4
unnamed: SW3.1, U1.6
unnamed: U1.9, Y1.3
unnamed: U1.10, Y1.1

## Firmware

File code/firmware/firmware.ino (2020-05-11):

// Ventmon - Ventilator Monitor
// Evan Widloski, Brian Ricconi
// 2020-04-09

#include <stdlib.h>
#include <stdbool.h>
#include <unistd.h>
#include <stdint.h>
#include <string.h>

// ----- Config -----

// pressure sensor sample rate, should divide 1000 evenly
const uint8_t SAMPLE_RATE = 100;

// pin configuration
const uint8_t PIN_MODE = 2;
const uint8_t PIN_UP = 0;
const uint8_t PIN_DOWN = 4;
const uint8_t PIN_BUZZ = 3;
const uint8_t PIN_PRES = A5;
const byte digit_pins[] = {A4, A2, A0, 11, 10};
const byte segment_pins[] = {6, 12, 7, A1, A3, 8, 9, 5};

// buzzer volume
const uint8_t volume = 5;

// button debounce time, milliseconds
const uint16_t debounce_time = 200;

#include "algorithm.h"
#include "display.h"
#include "alarm.h"

// ----- Main -----

// handle pin change interrupt for buttons
ISR (PCINT2_vect)
{
    // mode button press
    if ((PIND & (1 << PD0)) == 0 && debounce()) {
        mode_pressed = true;
    }
    // down button press
    if ((PIND & (1 << PD4)) == 0 && debounce()) {
        up_pressed = true;
    }
    // up button press
    if ((PIND & (1 << PD2)) == 0 && debounce()) {
        down_pressed = true;
    }
}


void setup() {
    Serial.begin(115200);
    Serial.println("start");
    // pressure input
    pinMode(A6, INPUT);
    pinMode(A7, INPUT);
    // button 1
    pinMode(PIN_MODE, INPUT);
    digitalWrite(PIN_MODE, HIGH);
    pci_setup(PIN_MODE);
    // button 2
    pinMode(PIN_UP, INPUT);
    digitalWrite(PIN_UP, HIGH);
    pci_setup(PIN_UP);
    // button 3
    pinMode(PIN_DOWN, INPUT);
    digitalWrite(PIN_DOWN, HIGH);
    pci_setup(PIN_DOWN);
    // buzzer
    pinMode(PIN_BUZZ, OUTPUT);
    analogWrite(PIN_BUZZ, 0);

    // set buzzer frequency to ~4kHz
    TCCR2B = TCCR2B & 0b11111000 | 0b00000010;

    // display pin initialization
    for(byte i = 0; i < sizeof(digit_pins); i++) {
        pinMode(digit_pins[i], OUTPUT);
    }
    for(byte i = 0; i < sizeof(segment_pins); i++) {
        pinMode(segment_pins[i], OUTPUT);
    }

    init_algorithm(SAMPLE_RATE);

}


void loop() {

    if (mode_pressed) {

        Serial.println("MODE pressed");
        mode_pressed = false;

        if (mode == MODE_ALARM) {
            // disable alarm
            alarm_raised = ALARM_NONE;
            analogWrite(PIN_BUZZ, 0);
            alarm_disabled = true;
            mode = MODE_DISPLAY;
        }
        else {
            mode = (mode + 1) % total_modes;
        }
    }
    if (millis() - last_sample >= (1000 / SAMPLE_RATE)) {
        last_sample = millis();

        if (mode == 0) {
            p = ADC2CM((float) analogRead(PIN_PRES));

            run_algorithm(p, SAMPLE_RATE);

            if(alarm_raised) {
                mode = MODE_ALARM;
            }

            // change displayed metric every few seconds
            if (counter < counter_max / 3) {
                // PIP
                sprintf(displayedValue, "PI:%2d", (uint8_t) limit(pip, 0, 99));
            }
            else if (counter < 2 * counter_max / 3) {
                // PEEP
                sprintf(displayedValue, "PE:%2d", (uint8_t) limit(peep, 0, 99));
            }
            else {
                // rate
                sprintf(
                    displayedValue,
                    "rr:%2d",
                    (uint8_t) limit(respiration_rate, 0, 99)
                );
            }

        }
        // edit non-cycling alarm condition
        else if (mode == MODE_SET_THRESH_NC) {
            // change alarm setting
            if (up_pressed) {
                THRESH_NC = limit(THRESH_NC, 0, 25) + 5;
                up_pressed = false;
            }
            else if (down_pressed) {
                THRESH_NC = limit(THRESH_NC, 5, 35) - 5;
                down_pressed = false;
            }
            // flash alarm setting
            if (counter % (SAMPLE_RATE / 2) > SAMPLE_RATE / 8) {
                sprintf(displayedValue, "NC:%2d", THRESH_NC);
            } else {
                sprintf(displayedValue, "NC:  ");
            }
        }
        // edit low-pressure alarm condition
        else if (mode == MODE_SET_THRESH_LP) {
            // change alarm setting
            if (up_pressed) {
                THRESH_LP = limit(THRESH_LP, 1, 19) + 1;
                up_pressed = false;
            }
            else if (down_pressed) {
                THRESH_LP = limit(THRESH_LP, 3, 21) - 1;
                down_pressed = false;
            }
            // flash alarm setting
            if (counter % (SAMPLE_RATE / 2) > SAMPLE_RATE / 8) {
                sprintf(displayedValue, "LP:%2d", THRESH_LP);
            } else {
                sprintf(displayedValue, "LP:  ");
            }
        }
        // edit high-pressure alarm condition
        else if (mode == MODE_SET_THRESH_HP) {
            // change alarm setting
            if (up_pressed) {
                THRESH_HP = limit(THRESH_HP, 25, 85) + 5;
                up_pressed = false;
            }
            else if (down_pressed) {
                THRESH_HP = limit(THRESH_HP, 35, 95) - 5;
                down_pressed = false;
            }
            // flash alarm setting
            if (counter % (SAMPLE_RATE / 2) > SAMPLE_RATE / 8) {
                sprintf(displayedValue, "HP:%2d", THRESH_HP);
            } else {
                sprintf(displayedValue, "HP:  ");
            }
        }
        // edit low-rate alarm condition
        else if (mode == MODE_SET_THRESH_LR) {
            // change alarm setting
            if (up_pressed) {
                THRESH_LP = limit(THRESH_LR, 4, 14) + 1;
                up_pressed = false;
            }
            else if (down_pressed) {
                THRESH_LP = limit(THRESH_LR, 6, 16) - 1;
                down_pressed = false;
            }
            // flash alarm setting
            if (counter % (SAMPLE_RATE / 2) > SAMPLE_RATE / 8) {
                sprintf(displayedValue, "Lr:%2d", THRESH_LR);
            } else {
                sprintf(displayedValue, "Lr:  ");
            }
        }
        // edit high-rate alarm condition
        else if (mode == MODE_SET_THRESH_HR) {
            // change alarm setting
            if (up_pressed) {
                THRESH_HR = limit(THRESH_HR, 10, 55) + 5;
                up_pressed = false;
            }
            else if (down_pressed) {
                THRESH_HR = limit(THRESH_HR, 20, 65) - 5;
                down_pressed = false;
            }
            // flash alarm setting
            if (counter % (SAMPLE_RATE / 2) > SAMPLE_RATE / 8) {
                sprintf(displayedValue, "Hr:%2d", THRESH_HR);
            } else {
                sprintf(displayedValue, "Hr:  ");
            }
        }
        // alarm mode
        else if (mode == MODE_ALARM) {
            // beep alarm on-off
            if (counter % SAMPLE_RATE > SAMPLE_RATE / 2) {
                analogWrite(PIN_BUZZ, volume);
            }
            else {
                analogWrite(PIN_BUZZ, 0);
            }
            // flash alarm code
            if (counter % (SAMPLE_RATE / 2) > SAMPLE_RATE / 8) {
                sprintf(
                    displayedValue,
                    "%s:%2d",
                    alarm_code,
                    (uint8_t) limit(alarm_value, 0, 99)
                );
            }
            else {
                sprintf(displayedValue, "     ");
            }
        }

        counter++;
        counter %= counter_max;
    }

    update_display();

}

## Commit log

2020-04-03 add debug printing
2020-04-07 update sample data
2020-04-07 add design files
    [cost_analysis.ods, pcb_dip-B_Cu.gbl, pcb_dip-B_Mask.gbs, pcb_dip-B_Paste.gbp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]
2020-04-07 better ground plane
    [pcb_dip.kicad_pcb]
2020-04-07 add prototype design
    [pcb_dip-B_Cu.gbl, pcb_dip-B_Mask.gbs, pcb_dip-B_Paste.gbp, pcb_dip-B_SilkS.gbo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]
2020-04-07 update gerbers
    [pcb_proto-B_Cu.gbl, pcb_proto-B_Mask.gbs, pcb_proto-B_Paste.gbp, pcb_proto-B_SilkS.gbo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]
2020-04-14 update gitignore
    [pcb_dip-B_Cu.gbl, pcb_dip-B_Mask.gbs, pcb_dip-B_Paste.gbp, pcb_dip-B_SilkS.gbo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]
2020-04-14 update through hole board
    [pcb_dip-B_Cu.gbl, pcb_dip-B_Mask.gbs, pcb_dip-B_Paste.gbp, pcb_dip-B_SilkS.gbo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]
2020-04-14 purge old files
    [enclosure.FCStd, pcb_smd-B_Cu.gbr, pcb_smd-B_Mask.gbr, pcb_smd-B_Paste.gbr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]
2020-04-14 update readme repo structure
    [enclosure.FCStd]
2020-04-16 Updated pressure and rate tracking algorithm
2020-04-17 3d printable enclosure
    [bottom.stl, top.stl]
2020-04-17 wider holes on pogo footprint
2020-04-17 remove gerbers
    [pcb_proto.kicad_pcb, pcb_proto.sch, pcb_smd-B_Cu.gbr, pcb_smd-B_Mask.gbr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]
2020-04-17 add schematic, remove gerbers
    [pcb_smd.kicad_pcb]
2020-04-23 Tekmill Files
    [92949A107_18-8 SS BUTTON HEAD HEX DRIVE SCREW.SLDPRT, 92949A192_18-8 SS BUTTON HEAD HEX DRIVE SCREW.SLDPRT, MCH-00647.DXF, MCH-00647.SLDDRW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]
2020-04-24 button order
    [pcb_proto.kicad_pcb, pcb_proto.sch]
2020-04-25 add converted data files
    [exit_port_leak.csv, first_test.csv, low_flow.csv, low_rate.csv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]
2020-05-11 dont symlink, pass sample_rate as arg
2020-05-22 convert to CMH2O
    [exit_port_leak.csv, first_test.csv, low_flow.csv, low_rate.csv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]
2020-05-22 switch pogo size
    [pcb_smd.kicad_pcb, pcb_smd.sch]
2020-05-31 make true pip peep rr values accessible
    [exit_port_leak.csv, first_test.csv, low_flow.csv, low_rate.csv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]
2020-06-19 finish smd version
    [pcb_smd.kicad_pcb, pcb_smd.sch]
2020-07-02 fix TX pin, fix VBUS
    [pcb_smd.kicad_pcb, pcb_smd.sch]
